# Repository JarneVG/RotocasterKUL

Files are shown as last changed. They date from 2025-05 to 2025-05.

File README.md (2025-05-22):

# RotocasterKUL
This is the accompanying report and documentation for the rotocasting machine, made in 2025 for the KU Leuven soft robotics research team.

## Software
Here, you can find the main code under RotocasterMainFirmware (arduino .ino files) as well as other people's libraries used for this project.

I changed some of these libraries to add or change functionalities, so be sure to add the ones you find here to your Arduino -> libraries directory

You should also have the Earle Philhowers Arduino Pico core installed.

Some useful tutorials for uploading:

https://learn.adafruit.com/rp2040-arduino-with-the-earlephilhower-core/installing-the-earlephilhower-core

https://randomnerdtutorials.com/programming-raspberry-pi-pico-w-arduino-ide/

## Electrical Hardware
The KiCAD design files can be found here. If there is something that needs to change, you can find the current version of the project here. The small problems with the current version are already implemented.

## Mechanical Hardware
A .step file is uploaded here to get a better grasp of what might be going on under the covers. This is not a build guide, rather part of the documentation.
Same thing for the bill of materials, where you can find all the parts used in this project

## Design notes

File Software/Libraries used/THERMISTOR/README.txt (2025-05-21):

## Original repository

https://github.com/panStamp/thermistor.git

Basic library that reads a NTC thermistor from an analog pin. Calculations relie on
Steinhart–Hart equation:

https://en.wikipedia.org/wiki/Thermistor#Steinhart.E2.80.93Hart_equation

See the example for more information.

Example of use with panStamp:
https://github.com/panStamp/panstamp/wiki/Temperature-measurement-with-cheap-NTC's

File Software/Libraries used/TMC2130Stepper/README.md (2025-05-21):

## Original repository

https://github.com/teemuatlut/TMC2130Stepper.git

# TMC2130Stepper
Arduino library for Trinamic TMC2130 Stepper driver

## TODO:
- [ ] Comments
- [x] Documentation
- [x] Examples
- [x] Easy setup for NEMA17 with default settings
- [x] Convert functions returning 0/1 to boolean
- [ ] Fritzing image of the wiring for an example setup

## Installation:

Use the Arduino IDE library manager (Sketch -> Include library -> Manage libraries...)

Search for TMC2130Stepper and then install.

Or download the zip file from Github and extract it to<br>
your-scetchbook-location/libraries<br>
and restart the IDE.

or goto to you arduino libraries folder and in command line
    git clone https://github.com/teemuatlut/TMC2130Stepper.git

## What works:
Nearly all the features in the registeries are configurable through get/set functions. See below for a list of functions. Datasheet ([link](https://www.trinamic.com/fileadmin/assets/Products/ICs_Documents/TMC2130_datasheet.pdf)) from Trinamic also provides further detail into the settings available.

## Simple example
```cpp
/*
Initializes the library and turns the motor in alternating directions.
*/
#define EN_PIN    38  // Nano v3:	16 Mega:	38	//enable (CFG6)
#define DIR_PIN   55  //			19			55	//direction
#define STEP_PIN  54  //			18			54	//step
#define CS_PIN    40  //			17			64	//chip select

bool dir = true;

#include <TMC2130Stepper.h>
TMC2130Stepper TMC2130 = TMC2130Stepper(EN_PIN, DIR_PIN, STEP_PIN, CS_PIN);

void setup() {
	Serial.begin(9600);
	TMC2130.begin(); // Initiate pins and registeries
	TMC2130.SilentStepStick2130(600); // Set stepper current to 600mA
	TMC2130.stealthChop(1); // Enable extremely quiet stepping
	
	digitalWrite(EN_PIN, LOW);
}

void loop() {
	digitalWrite(STEP_PIN, HIGH);
	delayMicroseconds(10);
	digitalWrite(STEP_PIN, LOW);
	delayMicroseconds(10);
	uint32_t ms = millis();
	static uint32_t last_time = 0;
	if ((ms - last_time) > 2000) {
		if (dir) {
			Serial.println("Dir -> 0");
			TMC2130.shaft_dir(0);
		} else {
			Serial.println("Dir -> 1");
			TMC2130.shaft_dir(1);
		}
		dir = !dir;
		Serial.println(TMC2130.GCONF(), BIN);
		last_time = ms;
	}
}
```

## Current calculations

A simple way to set the current is to use the setCurrent() method.

    I_rms = (CS+1)/32 * V_fs/(R_sense+0.02mOhm) * 1/sqrt(2)
    I_motor = I_sine/248 * (CS+1/32) * V_fs/(R_sense+0.02mOhm)

Where:<br>
I_rms is the rms current<br>
I_motor is the motor current<br>
CS is the Current Scale value<br>
V_fs is the voltage determined by v_sense<br>
R_sense is the chosen sense resistor<br>
I_sine is the current position in the sine table. I_motor reaches peak value at I_sine = 248<p>

If external_ref is enabled, V_fs is scaled by V_ain/2.5V

## Functions

Function 			| Argument range | Returns | Description
--------------------|-----|---|-----------------------------
begin 				|  -  | - | Initialized pins Enable, Direction, Step and Chip Select.<br>Initialized the SPI pins MOSI, MISO and SCK.<br>Calls spi.begin()<br>Sets off_time = 2 and blank_time = 24
setCurrent			|  0..2000<br>0.1 .. 1<br>0..1 | - | Helper function to set the motor RMS current.<br>Arguments:<br><b>uint16_t</b> Desired current in milliamps<br><b>float</b> Sense resistor value<br><b>float</b> Multiplier for holding current<br>Example for SilentStepStick2130: setCurrent(1200, 0.11, 0.5)<p>Makes use of the run_current() and hold_current() funtions.
SilentStepStick2130 |  0..2000  | - | Calls the begin() functions and according to the argument sets the current with sense resistor being 0.11 and multiplier being 0.5

## Register functions:

Note: You can read the saved value by calling a function without providing an argument.

### GCONF register
Function 			| Argument range | Returns | Description
--------------------|-----|---------|-----------------------------
GCONF 				|  -  | uint32_t| Read actual bits from the register
external_ref 		| 0/1 | bool | Use external voltage reference for coil currents
internal_sense_R 	| 0/1 | bool | Use internal sense resistors
stealthChop 		| 0/1 | bool | Enable stealthChop (dependant on velocity thresholds)
commutation 		| 0/1 | bool | Enable commutation by full step encoder
shaft_dir 			| 0/1 | bool | Inverse motor direction
diag0_errors 		| 0/1 | bool | Enable DIAG0 active on driver errors: Over temperature (ot), short to GND (s2g), undervoltage chargepump (uv_cp)
diag0_temp_prewarn 	| 0/1 | bool | Enable DIAG0 active on driver over temperature prewarning
diag0_stall 		| 0/1 | bool | Enable DIAG0 active on motor stall (set TCOOLTHRS before using this feature)
diag1_stall 		| 0/1 | bool | Enable DIAG1 active on motor stall (set TCOOLTHRS before using this feature) 
diag1_index 		| 0/1 | bool | Enable DIAG1 active on index position (microstep look up table position 0) 
diag1_chopper_on 	| 0/1 | bool | Enable DIAG1 active when chopper is on
diag1_steps_skipped | 0/1 | bool | Enable output toggle when steps are skipped in dcStep mode (increment of LOST_STEPS). Do not enable in conjunction with other DIAG1 options. 
diag0_active_high 	| 0/1 | bool | Set DIAG0 to active high
diag1_active_high 	| 0/1 | bool | Set DIAG1 to active high
small_hysteresis 	| 0/1 | bool | <b>0:</b> Hysteresis for step frequency comparison is 1/16 <br><b>1:</b> Hysteresis for step frequency comparison is 1/32
stop_enable 		| 0/1 | bool | Emergency stop: DCIN stops the sequencer when tied high (no steps become executed by the sequencer, motor goes to standstill state).
direct_mode 		| 0/1 | bool | Motor coil currents and polarity are directly controlled by the SPI interface.

### IHOLD_IRUN register
Function 		| Argument 	| Returns | Description
----------------|-----------|---------|-----------------------------
hold_current 	| 0..31 	| uint8_t | Standstill current (0=1/32…31=32/32)
run_current 	| 0..31 	| uint8_t | Motor run current (0=1/32…31=32/32)
hold_delay 		| 0..15 	| uint8_t | Controls the number of clock cycles for motor power down after a motion as soon as standstill is detected (stst=1) and TPOWERDOWN has expired. 

### REG_TPOWERDOWN register
Function 		 | Argument | Returns 	| Description
-----------------|----------|-----------|-----------------------------
power_down_delay | 0..255 	| uint8_t  	| power_down_delay sets the delay time after stand still (stst) of the motor to motor current power down. Time range is about 0 to 4 seconds. <br>0…((2^8)-1) * 2^18 tCLK 

### REG_TSTEP register
Function 		| Argument 	| Returns  | Description
----------------|-----------|----------|-----------------------------
microstep_time 	| - 		| uint32_t | Read the actual measured time between two 1/256 microsteps derived from the step input frequency in units of 1/fCLK. 

### REG_TPWMTHRS register
Function 			| Argument 		| Returns	| Description
--------------------|---------------|-----------|-----------------------------
stealth_max_speed 	| 0..1,048,575 	| uint32_t 	| This is the upper velocity for stealthChop voltage PWM mode. TSTEP ≥ TPWMTHRS - stealthChop PWM mode is enabled, if configured - dcStep is disabled 

### REG_TCOOLTHRS register
Function 			| Argument 		| Returns 	| Description
--------------------|---------------|-----------|-----------------------------
coolstep_min_speed 	| 0..1,048,575 	| uint32_t 	| This is the lower threshold velocity for switching on smart energy coolStep and stallGuard feature. 

### REG_THIGH register
Function 		| Argument 		| Returns 	| Description
----------------|---------------|-----------|-----------------------------
mode_sw_speed 	| 0..1,048,575 	| uint32_t  | This velocity setting allows velocity dependent switching into a different chopper mode and fullstepping to maximize torque. 

### REG_XDRIRECT register
Function 		| Argument 		| Returns 	| Description
----------------|---------------|-----------|-----------------------------
coil_A_current 	| -255..+255 	| int16_t  	| Specifies Motor coil currents and polarity directly programmed via the serial interface. In this mode, the current is scaled by IHOLD setting. 
coil_B_current 	| -255..+255 	| int16_t  	| As above.

### REG_VDCMIN register
Function 			| Argument 		| Returns 	| Description
--------------------|---------------|-----------|-----------------------------
DCstep_min_speed 	| 0..8,388,607 	| uint32_t  | The automatic commutation dcStep becomes enabled by the external signal DCEN. VDCMIN is used as the minimum step velocity when the motor is heavily loaded. <br>Hint: Also set DCCTRL parameters in order to operate dcStep.

### REG_CHOPCONF register
Function 				| Argument  | Returns 	| Description
------------------------|-----------|-----------|-----------------------------
CHOPCONF 				| - 		| uint32_t 	| Read actual bits from the register
off_time 				| 0..15 	| uint8_t 	| Off time setting controls duration of slow decay phase<br>NCLK= 12 + 32*TOFF<br>Initialized to value 2 (NCLK = 76) by begin()
hysteresis_start 		| 1..8 		| uint8_t 	| Add 1, 2, …, 8 to hysteresis low value HEND (1/512 of this setting adds to current setting) Attention: Effective HEND+HSTRT ≤ 16. Hint: Hysteresis decrement is done each 16 clocks
fast_decay_time 		| 0..15 	| uint8_t 	| Fast decay time setting TFD with  NCLK= 32*HSTRT
hysteresis_end 			| -3..12	| int8_t 	| This is the hysteresis value which becomes used for the hysteresis chopper. 
sine_offset 			| -3..12	| int8_t 	| This is the sine wave offset and 1/512 of the value becomes added to the absolute value of each sine wave entry.
disable_I_comparator 	| 0/1		| bool 	| <b>1:</b> Disables current comparator usage for termination of the fast decay cycle.<br>chopper_mode needs to be 1.
random_off_time 		| 0/1		| bool 	| <b>0:</b> Chopper off time is fixed as set by TOFF <br><b>1:</b> Random mode, TOFF is random modulated by dNCLK= -12 … +3 clocks. 
chopper_mode 			| 0/1		| uint8_t 	| <b>0:</b> Standard mode (spreadCycle) <br><b>1:</b> Constant off time with fast decay time.  <br>Fast decay time is also terminated when the negative nominal current is reached. Fast decay is after on time. 
blank_time 				| 16, 24,<br>36, 54| uint8_t | Set comparator blank time to 16, 24, 36 or 54 clocks. <br>Hint: 24 or 36 is recommended for most applications<br>Initialized to 36 (register value = 3) by begin()
high_sense_R 			| 0/1 		| bool 	| <b>0:</b> Low sensitivity, high sense resistor voltage <br><b>1:</b> High sensitivity, low sense resistor voltage 
fullstep_threshold 		| 0/1		| bool 	| This bit enables switching to fullstep, when VHIGH is exceeded. Switching takes place only at 45° position. The fullstep target current uses the current value from the microstep table at the 45° position. 
high_speed_mode 		| 0/1		| bool 	| This bit enables switching to chm=1 and fd=0, when VHIGH is exceeded. This way, a higher velocity can be achieved. Can be combined with vhighfs=1. If set, the TOFF setting automatically becomes doubled during high velocity operation in order to avoid doubling of the chopper frequency. 
sync_phases 			| 0..15		| bool 	| Synchronization of the chopper for both phases of a two phase motor in order to avoid the occurrence of a beat, especially at low motor velocities. It is automatically switched off above VHIGH.
microsteps 				| 255, 128, 64, 32, 16,<br>8, 4, 2, 0 (FULLSTEP) | uint8_t | Reduced microstep resolution for Step/Dir operation. The resolution gives the number of microstep entries per sine quarter wave.
interpolate 			| 0/1 		| bool 	| The actual microstep resolution becomes extrapolated to 256 microsteps for smoothest motor operation.
double_edge_step 		| 0/1 		| bool 	| Enable step impulse at each step edge to reduce step frequency requirement. 
disable_short_protection| 0/1 		| bool 	| <b>0:</b> Short to GND protection is on <br><b>1:</b> Short to GND protection is disabled 

### REG_COOLCONF register
Function 			| Argument 	 | Returns  | Description
--------------------|------------|----------|-----------------------------
COOLCONF 			| - 		 | uint32_t | Read actual bits from the register
sg_min 				| 0..15 	 | uint8_t 	| If the stallGuard2 result falls below sg_min*32, the motor current becomes increased to reduce motor load angle.
sg_max 				| 0..15 	 | uint8_t 	| If the stallGuard2 result is equal to or above (sg_min+sg_max+1)*32, the motor current becomes decreased to save energy. 
sg_step_width 		| 1, 2, 4, 8 | uint8_t 	| Current increment steps per measured stallGuard2 value
sg_current_decrease | 1, 2, 8, 32| uint8_t 	| For each (value) stallGuard2 values decrease by one 
smart_min_current 	| uint8_t 	 | uint8_t 	| <b>0:</b> 1/2 of current setting (IRUN)<br><b>1:</b> 1/4 of current setting (IRUN) 
sg_stall_value		| int8_t 	 | int8_t  	| This signed value controls stallGuard2 level for stall output and sets the optimum measurement range for readout. A lower value gives a higher sensitivity. Zero is the starting value working with most motors.  -64 to +63:  A higher value makes stallGuard2 less sensitive and requires more torque to indicate a stall. 
sg_filter 			| uint8_t 	 | uint8_t 	| <b>0:</b> Standard mode, high time resolution for stallGuard2<br><b>1:</b> Filtered mode, stallGuard2 signal updated for each four fullsteps (resp. six fullsteps for 3 phase motor) only to compensate for motor pole tolerances 

### REG_PWMCONF register
Function | Argument | Returns | Description
--------------------|-----------|----------|-----------------------------
PWMCONF 			| - 		| uint32_t | Read actual bits from the register
stealth_amplitude 	| 0..255 	| uint8_t  | pwm_ autoscale=0 <br>User defined  PWM amplitude offset (0-255) The resulting amplitude (limited to 0…255) is: PWM_AMPL + PWM_GRAD * 256 / TSTEP <p>pwm_ autoscale=1 <br>User defined maximum PWM amplitude when switching back from current chopper mode to voltage PWM mode (switch over velocity defined by TPWMTHRS). Do not set too low values, as the regulation cannot measure the current when the actual PWM value goes below a setting specific value. Settings above 0x40 recommended. 
stealth_gradient 	| 0..255 	| uint8_t  | pwm_ autoscale=0 <br>Velocity dependent gradient for PWM amplitude:  PWM_GRAD * 256 / TSTEP  is added to PWM_AMPL <p>pwm_ autoscale=1 <br>User defined  maximum PWM amplitude change per half wave (1 to 15) 
stealth_freq 		| 0..3 		| uint8_t  | <b>0:</b> fPWM=2/1024 fCLK<br><b>1:</b> fPWM=2/683 fCLK<br><b>2:</b> fPWM=2/512 fCLK<br><b>3:</b> fPWM=2/410 fCLK
stealth_autoscale 	| 0/1		| bool     | <b>0:</b> User defined PWM amplitude. The current settings have no influence.<br><b>1:</b> Enable automatic current control Attention: When using a user defined sine wave table, the amplitude of this sine wave table should not be less than 244. Best results are obtained with 247 to 252 as peak values.
stealth_symmetric 	| 0/1	 	| bool     | <b>0:</b> The PWM value may change within each PWM cycle (standard mode)<br><b>1:</b> A symmetric PWM cycle is enforced 
standstill_mode 	| 0..3		| uint8_t  | Stand still option when motor current setting is zero (I_HOLD=0).<br><b>0:</b>  Normal operation<br><b>1:</b>  Freewheeling<br><b>2:</b> Coil shorted using LS drivers<br><b>3:</b>  Coil shorted using HS drivers 

### REG_DRVSTATUS register
Function 	| Argument 	| Returns 	| Description
------------|-----------|-----------|-----------------------------
DRVSTATUS 	| - 		| uint32_t 	| Read actual bits from the register

### REG_PWM_SCALE register
Function 	| Argument 	| Returns 	| Description
------------|-----------|-----------|-----------------------------
PWM_SCALE 	| - 		| uint32_t 	| Read actual bits from the register

### REG_ENCM_CTRL register
Function 		| Argument 	| Returns 	| Description
----------------|-----------|-----------|-----------------------------
invert_encoder 	| 0/1 		| bool  	| Invert encoder inputs
maxspeed 		| 0/1	 	| bool  	| Ignore Step input. If set, the hold current IHOLD determines the motor current, unless a step source is activated

### REG_LOST_STEPS register
Function 	| Argument 	| Returns 	| Description
------------|-----------|-----------|-----------------------------
LOST_STEPS 	| - 		| uint32_t 	| Read actual bits from the register

### Read raw registry:

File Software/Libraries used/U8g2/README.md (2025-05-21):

# Original repository

https://github.com/ArduinoGetStarted/buzzer.git

# U8g2_Arduino: Arduino Monochrome Graphics Library

https://raw.githubusercontent.com/wiki/olikraus/u8g2/img/uc1701_dogs102_uno_board_320.jpg 

U8glib V2 library for Arduino

Description: https://github.com/olikraus/u8g2/wiki

Issue Tracker: https://github.com/olikraus/u8g2/issues

Download (2.35.30): https://github.com/olikraus/U8g2_Arduino/archive/master.zip

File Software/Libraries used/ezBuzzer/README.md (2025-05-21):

## Original repository

https://github.com/ArduinoGetStarted/buzzer.git

## Buzzer Library for Arduino - ezBuzzer
This library is designed for buzzer to beep or play memody without blocking other code.

**ezBuzzer** stands for **easy buzzer**, which mean that the library is easy to use.

Features
----------------------------
* Supports beep
* Supports melody
* All functions are non-blocking (no delay() function)

Available Examples
----------------------------
* [Beep](https://arduinogetstarted.com/library/arduino-beep-example)
* [Melody](https://arduinogetstarted.com/library/arduino-melody-example)
* [MelodyRepeat](https://arduinogetstarted.com/library/arduino-melody-repeat-example)

Available Functions
----------------------------
* ezBuzzer()
* stop()
* beep()
* playMelody()
* getState()
* loop()

How To Install the Library
----------------------------
* [ezBuzzer Library Installization Guide](https://arduinogetstarted.com/tutorials/arduino-buzzer-library)

References
----------------------------
* [ezBuzzer Library Reference](https://arduinogetstarted.com/tutorials/arduino-buzzer-library)

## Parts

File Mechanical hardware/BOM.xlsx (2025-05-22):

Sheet: BOM
item nr | Category | Part | Supplier Part # | Number | # needed | Cost/Article | Total cost | Supplier | Date of order | Date of arrival | Link | Idx
 | Electrical |  |  |  |  |  |  |  |  |  |  | 1
 | Interface |  |  | €30.91 |  |  |  |  |  |  |  | 2
1 |  | Rotary push button |  | 1 | 1 | €2.63 | €2.63 | Farnell | 2025-02-28 | 2025-03-06 | https://be.farnell.com/bourns/pec11l-4120f-s0020/encoder-quadrature-20ppr-60rpm/dp/4014825 | 3
2 |  | Oled screen .95" |  | 1 | 1 | €17.29 | €17.29 | Farnell | 2025-02-28 |  |  | 4
3 |  | LCD screen | 2436023 - 62 | 1 | 1 | €10.99 | €10.99 | Conrad | 2025-03-26 | 2025-04-03 | https://www.conrad.be/nl/p/joy-it-lc-display-wit-blauw-128-x-64-pixel-b-x-h-x-d-93-x-70-x-12-mm-2436023.html | 5
 |  |  |  |  |  |  |  |  |  |  |  | 6
 | Safety |  |  | €49.43 |  |  |  |  |  |  |  | 7
4 |  | Door limit switch | DEL00005 | 1 | 1 | €3.85 | €3.85 | 123-3D | 2025-03-26 | 2024-04-10 | https://www.123-3d.nl/123-3D-Microswitch-eindstop-met-1-meter-kabel-i1725-t324.html | 8 | https://www.123-3d.nl/123-3D-Microswitch-eindstop-i974-t324.html
5 |  | E-stop | 2748226 | 1 | 1 | €12.98 | €12.98 | Farnell | 2025-03-26 | 2025-04-03 | https://be.farnell.com/multicomp-pro/mca20l-v4e10q7r/emergency-stop-sw-spst-no-120v/dp/2748226 | 9 | https://benl.rs-online.com/web/p/emergency-stop-push-buttons/0102713
6 |  | Actual E-stop | 704622 - 62 | 1 | 1 | €9.49 | €9.49 | Conrad |  | 2025-04-22 | https://www.conrad.be/nl/p/tru-components-las0-a3y-11ts-noodstopschakelaar-250-v-ac-5-a-1x-nc-1x-no-ip40-1-stuk-s-704622.html | 10
7 |  | Resettable fuse for heater | 2786604 | 1 | 1 | €1.28 | €1.28 | farnell | 2025-03-26 | 2025-04-03 | https://nl.farnell.com/littelfuse/ahef750/fuse-resettable-ptc-32vdc-7-5a/dp/2786604 | 11
8 |  | Fuse holder 20A |  | 1 | 1 | €1.08 | €1.08 | RS Components |  | 2025-04-22 | https://benl.rs-online.com/web/p/fuse-blocks/1884617?gb=s | 12
9 |  | Car fuse for heater 20A | 787-4151P | 10 | 1 | €0.28 | €2.81 | RS Components |  | 2025-04-22 | https://benl.rs-online.com/web/p/car-fuses/7874151P?gb=s | 13
 |  |  |  |  |  |  |  |  |  |  |  | 14
 | Heating |  |  | €28.94 |  |  |  |  |  |  |  | 15
10 |  | Heater + fan | B07Y24KVPQ | 1 | 1 | €13.09 | €13.09 | Amazon NL | 2025-03-26 | 2025-04-03 | https://www.amazon.nl/Constante-Temperatuur-PTC-ventilator-Autoverwarmer-Ruimteverwarmingsincubator/dp/B07YTL7DFK?__mk_nl_NL=%C3%85M%C3%85%C5%BD%C3%95%C3%91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 (https://www.amazon.nl/-/en/Nikou-Air-Heater-Constant-Temperature/dp/B07Y24KVPQ) | 16
11 |  | Thermo sensor (thermistor) | 4128286 | 1 | 1 | €4.85 | €4.85 | Farnell | 2025-03-26 | 2025-04-03 | https://be.farnell.com/molex/218534-3617/thermistor-ntc-3600k-10-kohm/dp/4128286 | 17
12 |  | Heat sink TO-220 | 189-9132 | 1 | 1 | €1.52 | €1.52 | RS Components | 2025-03-26 | 2025-04-04 | https://benl.rs-online.com/web/p/heatsinks/1899132?matchtype=&gad_source=1&gclsrc=aw.ds | 18
13 |  | Heat sink Pico | 3133389 - 62 | 1 | 1 | €1.49 | €1.49 | Conrad | 2025-03-26 | 2025-04-03 | https://www.conrad.be/nl/p/joy-it-rb-heatsink-b-koellichaamset-geschikt-voor-serie-raspberry-pi-banana-pi-asus-tinker-board-radxa-zwart-3133389.html | 19
14 |  | Pico cooling fan | 1720600 - 62 | 1 | 1 | €3.29 | €3.29 | Conrad | 2025-03-26 | 2025-04-03 | https://www.conrad.be/nl/p/joy-it-sbc-fan-303010-actieve-ventilator-geschikt-voor-serie-raspberry-pi-rock-pi-banana-pi-zwart-1720600.html | 20
15 |  | Electronics cooling fan | DMO00037 | 1 | 1 | €4.70 | €4.70 | 123-3D |  | 2025-04-22 | https://www.123-3d.nl/123-3D-Ventilator-24V-50x50x12-mm-axiaal-i2705-t15055.html | 21
 |  |  |  |  |  |  |  |  |  |  |  | 22 | https://www.tinytronics.nl/nl/mechanica-en-actuatoren/motoraansturingen-en-drivers/stappen-motoraansturingen-en-drivers/bigtreetech-tmc2130-v3.0-stappenmotord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
 | Compute |  |  | €39.64 |  |  |  |  |  |  |  | 23
16 |  | Stepper driver |  | 2 | 2 | €17.50 | €35.00 | 123-3D | 2025-03-26 | 2024-04-10 | https://www.123-3d.nl/BigTreeTech-TMC2130-Stappendriver-1-256-stap-interpolatie-v3-0-SPI-1020000132-ZZB000296-i8343-t332.html | 24
17 |  | Raspberry Pi Pico | 3643332 | 1 | 1 | €4.64 | €4.64 | Farnell | 2025-03-26 | 2025-04-03 | https://be.farnell.com/raspberry-pi/raspberry-pi-pico/raspberry-pi-32bit-arm-cortex/dp/3643332 | 25
 |  |  |  |  |  |  |  |  |  |  |  | 26
 | Power |  |  | €52.33 |  |  |  |  |  |  |  | 27
18 |  | Main power supply (220AC -> 24DC) | B077CK3NXY | 1 | 1 | €36.99 | €36.99 | Amazon BE | 2025-03-26 | 2025-04-03 | https://www.amazon.com.be/-/nl/industri%C3%ABle-omvormer-elektrische-printer-verwarming/dp/B077CK3NXY | 28
19 |  | Arduino power supply (24DC -> 5 DC) | DAR00071 | 1 | 1 | €6.05 | €6.05 | 123-3D | 2025-03-26 | 2024-04-10 | https://www.123-3d.nl/123-3D-Step-down-DC-DC-converter-3-2-40-V-DC-naar-1-25-35-V-DC-2-A-i3869-t13129.html | 29
20 |  | IEC C14 power socket with fuse & switch | 501638 - 62 | 1 | 1 | €5.00 | €5.00 | Conrad | 2025-03-26 | 2025-04-03 | https://www.conrad.be/nl/p/501638-apparaatstekker-koud-stekker-inbouw-verticaal-totaal-aantal-polen-2-pe-10-a-zwart-1-stuk-s-501638.html | 30
21 |  | Power cable 2m EU socket to IEC C13 | 2521346 - 62 | 1 | 1 | €4.29 | €4.29 | Conrad | 2025-03-26 | 2025-04-03 | https://www.conrad.be/nl/p/sygonix-sy-5042692-apparaat-koud-aansluitkabel-zwart-2-00-m-2521346.html | 31
 |  |  |  |  |  |  |  |  |  |  |  | 32
 | PCB |  |  | €15.02 |  |  |  |  |  | 2025-04-22 |  | 33
22 |  | n mosfet IRLZ44N | 162877 - 62 | 3 | 3 | €0.93 | €2.79 | Conrad | 2025-03-26 | 2025-04-03 | https://www.conrad.be/nl/p/infineon-technologies-irlz44npbf-mosfet-1-hexfet-110-w-to-220-162877.html | 34
23 |  | n mosfet IRL3705NPBF | 162784 - 62 | 1 | 1 | €2.29 | €2.29 | Conrad | 2025-03-26 | 2025-04-03 | https://www.conrad.nl/nl/p/infineon-technologies-irl3705npbf-mosfet-1-n-kanaal-170-w-to-220-162784.html | 35
24 |  | n mosfet IRLB3034PBF Low RdsOn | 161162 - 62 | 1 | 1 | €3.99 | €3.99 | Conrad |  | 2025-04-22 | https://www.conrad.be/nl/p/infineon-technologies-irlb3034pbf-mosfet-1-n-kanaal-375-w-to-220ab-161162.html?gad_source=1 | 36
25 |  | 100nF 0603 capacitors | 257-1091 | 50 | 8 | €0.03 | €1.40 | RS Components | 2025-03-26 | 2025-04-04 | https://benl.rs-online.com/web/p/mlccs-multilayer-ceramic-capacitors/2571091?gb=s | 37
26 |  | 10k 0603 resistors | 199-1659 | 20 | 12 | €0.03 | €0.64 | RS Components | 2025-03-26 | 2025-04-04 | https://benl.rs-online.com/web/p/surface-mount-resistors/1991659?gb=s | 38
27 |  | LED Strip 1m, 24VDC, Natural White |  | 1 | 1 | €3.91 | €3.91 | AliExpress | 2025-03-26 | 2025-04-03 | https://www.aliexpress.com/item/1005005576519990.html?mp=1 | 39
 |  |  |  |  |  |  |  |  |  |  |  | 40
 | Connectors |  |  | €20.56 |  |  |  |  |  |  |  | 41
28 |  | Female header (40 pins) | 1303521 - 62 | 5 | 3 | €0.75 | €3.75 | Conrad | 2025-03-26 | 2025-04-03 | https://www.conrad.be/nl/p/econ-connect-female-header-standaard-aantal-rijen-1-aantal-polen-per-rij-40-bl40-1g8-1-stuk-s-1303521.html | 42
29 |  | Male header (30 pins) | 1390106 - 62 | 7 | 2 | €0.44 | €3.08 | Conrad | 2025-03-26 | 2025-04-03 | https://www.conrad.be/nl/p/connfly-male-header-standaard-aantal-rijen-1-aantal-polen-per-rij-30-ds1021-1-30sf11-1-stuk-s-1390106.html | 43
30 |  | JST XH 4p Male 2.5mm | 820-1551 | 5 | 4 | €0.25 | €1.25 | RS Components | 2025-03-26 | 2025-04-04 | https://benl.rs-online.com/web/p/pcb-headers/8201551?gb=s | 44
31 |  | JST XH 4p Female 2.5mm | 820-1618 | 5 | 4 | €0.13 | €0.63 | RS Components | 2025-03-26 | 2025-04-04 | https://benl.rs-online.com/web/p/wire-housings-plugs/8201618?gb=s | 45
32 |  | JST XH 5p Male 2.5mm | 820-1560 | 5 | 1 | €0.32 | €1.61 | RS Components | 2025-03-26 |  | https://benl.rs-online.com/web/p/pcb-headers/8201560?gb=s | 46
33 |  | JST XH 5p Female 2.5mm | 820-1627 | 5 | 1 | €0.15 | €0.76 | RS Components | 2025-03-26 | 2025-04-04 | https://benl.rs-online.com/web/p/wire-housings-plugs/8201627?gb=s | 47
34 |  | JST XH 2p Male 2.5mm | 820-1554 | 5 | 2 | €0.18 | €0.92 | RS Components | 2025-03-26 | 2025-04-04 | https://benl.rs-online.com/web/p/pcb-headers/8201554?gb=s | 48
35 |  | JST XH 2p Female 2.5mm | 820-1611 | 5 | 2 | €0.11 | €0.55 | RS Components | 2025-03-26 | 2025-04-04 | https://benl.rs-online.com/web/p/wire-housings-plugs/8201611?gb=s | 49
36 |  | High Current Terminal Block | 790-1064 | 10 | 6 | €0.61 | €6.12 | RS Components | 2025-03-26 | 2025-04-04 | https://benl.rs-online.com/web/p/pcb-terminal-blocks/7901064?gb=s | 50
 |  |  |  |  |  |  |  |  |  |  |  | 51
37 |  | JST XH Female Crimp | 373-4188 | 100 | 25 | €0.02 | €1.90 | RS Components | 2025-03-26 | 2025-04-04 | https://benl.rs-online.com/web/p/crimp-contacts/3734188?gb=s | 52
38 |  | Thick current wires |  |  |  |  |  |  |  |  |  | 53
39 |  | 18 AWG Ferrules (to crimp wire ends) | 2758836 | 20 | 12 | €0.08 | €1.65 | Farnell | 2025-03-26 | 2025-04-03 | https://be.farnell.com/en-BE/wago/216-203/terminal-wire-ferrule-18awg-red/dp/2758836 | 54
 |  |  |  |  |  |  |  |  |  |  |  | 55
 | subtotal (incl btw) |  |  |  |  |  | €218.90 | €172.93 |  |  |  | 56
 |  |  |  |  |  |  |  |  |  |  |  | 57
 | Mechanical |  |  |  |  |  |  |  |  |  |  | 58
 | Frame |  |  | €129.54 |  |  |  |  |  |  |  | 59
40 |  | 20x20 Aluminium extrusion 575 mm |  | 4 |  | €3.89 | €15.55 | Aluxprofile | 2025-03-26 | 2025-04-03 | https://www.aluxprofile.com/aluminium-slot-profile-2020-v-slot/a3663?filter=38 | 60
41 |  | 20x20 Aluminium extrusion 630 mm |  | 4 |  | €4.25 | €17.02 | Aluxprofile | 2025-03-26 | 2025-04-03 | https://www.aluxprofile.com/aluminium-slot-profile-2020-v-slot/a3663?filter=39 | 61
42 |  | 20x20 Aluminium extrusion 510 mm |  | 4 |  | €3.44 | €13.78 | Aluxprofile | 2025-03-26 | 2025-04-03 | https://www.aluxprofile.com/aluminium-slot-profile-2020-v-slot/a3663?filter=40 | 62
43 |  | 20x20 Aluminium extrusion 530 mm |  | 2 |  | €3.58 | €7.16 | Aluxprofile | 2025-03-26 | 2025-04-03 | https://www.aluxprofile.com/aluminium-slot-profile-2020-v-slot/a3663?filter=41 | 63
44 |  | 20x20 Aluminium extrusion 313 mm |  | 2 |  | €2.12 | €4.23 | Aluxprofile | 2025-03-26 | 2025-04-03 | https://www.aluxprofile.com/aluminium-slot-profile-2020-v-slot/a3663?filter=42 | 64
45 |  | 20x20 Aluminium extrusion 365 mm |  | 2 |  | €2.46 | €4.92 | Aluxprofile | 2025-03-26 | 2025-04-03 | https://www.aluxprofile.com/aluminium-slot-profile-2020-v-slot/a3663?filter=43 | 65
46 |  | 20x20 Aluminium extrusion 501 mm |  | 2 |  | €3.38 | €6.77 | Aluxprofile | 2025-03-26 | 2025-04-03 | https://www.aluxprofile.com/aluminium-slot-profile-2020-v-slot/a3663?filter=44 | 66
47 |  | 20x20 Aluminium extrusion 383 mm |  | 2 |  | €2.58 | €5.17 | Aluxprofile | 2025-03-26 | 2025-04-03 | https://www.aluxprofile.com/aluminium-slot-profile-2020-v-slot/a3663?filter=45 | 67
48 |  | Loctite blue 5ml | 442-3413 | 1 |  | €10.54 | €10.54 | RS Components | 2025-03-26 | 2025-04-04 | https://benl.rs-online.com/web/p/thread-lock/4423413?gb=s | 68
49 |  | Adjustable feet | 531001 | 4 |  | €0.80 | €3.20 | Misumi | 2025-03-26 | 2025-04-22 | https://uk.misumi-ec.com/vona2/detail/221006483028/?list=PageCategory | 69
50 |  | Slot covers 5m | DFC00177 | 5 | est ~23m | €7.34 | €36.70 | 123-3D | 2025-03-26 | 2024-04-10 | https://www.123-3d.nl/123-3D-Slot-cover-6-mm-voor-2020-profiel-Grijs-1-meter-i7488-t14575.html | 70
51 |  | End caps 10pc | DFC00108 | 1 |  | €4.50 | €4.50 | 123-3D | 2025-03-26 | 2024-04-10 | https://www.123-3d.nl/123-3D-Afdekkap-t-b-v-aluminium-profiel-20x20-10-stuks-123-3D-huismerk-091042S05-091332-i5256-t14575.html | 71
 |  |  |  |  |  |  |  |  |  |  |  | 72
 | Axles & bearings |  |  | €38.93 |  |  |  |  |  |  |  | 73
52 |  | 8mm precision rod 110 mm | PSFG8-110 | 1 |  | €4.94 | €4.94 | Misumi | 2025-03-26 | 2025-04-22 | https://uk.misumi-ec.com/vona2/detail/110302634310/ | 74
53 |  | 8mm precision rod 86 mm | PSFG8-86 | 1 |  | €3.08 | €3.08 | Misumi | 2025-03-26 | 2025-04-22 | https://uk.misumi-ec.com/vona2/detail/110302634310/ | 75
54 |  | 8mm precision rod 66 mm | PSFG8-66 | 1 |  | €3.08 | €3.08 | Misumi | 2025-03-26 | 2025-04-22 | https://uk.misumi-ec.com/vona2/detail/110302634310/ | 76
55 |  | 8mm precision rod 87 mm | PSFG8-87 | 1 |  | €3.08 | €3.08 | Misumi | 2025-03-26 | 2025-04-22 | https://uk.misumi-ec.com/vona2/detail/110302634310/ | 77
56 |  | KFL8 bearing flange block x2 | DFC00077 | 3 |  | €8.25 | €24.75 | 123-3D | 2025-03-26 | 2024-04-10 | https://www.123-3d.nl/123-3D-KFL8-lager-as-bevestiging-2-stuks-i3512-t13814.html | 78
 |  |  |  |  |  |  |  |  |  |  |  | 79
 | Belts & pulleys |  |  | €82.75 |  |  |  |  |  |  |  | 80
57 |  | GT2 pulley 60t 8mm bore 9mm belt | DME00112 | 2 |  | €10.00 | €20.00 | 123-3D | 2025-03-26 | 2024-04-10 | https://www.123-3d.nl/123-3D-GT2-Pulley-hoge-resolutie-9-mm-riem-60-tanden-8-mm-as-i2573-t14819.html | 81
58 |  | GT2 pulley 20t 8mm bore 9mm belt | DME00069 | 2 |  | €6.00 | €12.00 | 123-3D | 2025-03-26 | 2024-04-10 | https://www.123-3d.nl/123-3D-GT2-Pulley-hoge-resolutie-9-mm-riem-20-tanden-8-mm-as-i2306-t14819.html | 82
59 |  | GT2 pulley 20t 5mm bore 9mm belt | DME00068 | 2 |  | €6.00 | €12.00 | 123-3D | 2025-03-26 | 2024-04-10 | https://www.123-3d.nl/123-3D-GT2-Pulley-hoge-resolutie-9-mm-riem-20-tanden-5-mm-as-i2305-t14815.html | 83
60 |  | GT2 belt 9mm 726mm | GBN7262GT-90 | 2 |  | €11.45 | €22.90 | Misumi | 2025-03-26 | 2025-04-22 | https://uk.misumi-ec.com/vona2/detail/110302190510/ | 84
61 |  | GT2 belt 9mm 1078mm | 1078-2GT-9 | 0 |  | €20.11 | €0.00 | Misumi | 2025-03-26 |  | https://uk.misumi-ec.com/vona2/detail/221004924958/?list=PageCategory | 85
62 |  | GT2 belt 10mm 1040mm | 9mm/1040-2GT/1st | 1 |  | €3.53 | €3.53 | AliExpress | 2025-03-26 | 2025-04-03 | https://nl.aliexpress.com/item/32299384151.html?curPageLogUid=R1AIa9U5Uo5a&utparam-url=scene%3Asearch%7Cquery_from%3A | 86
63 |  | Flanged bearing 606HZZ1 | F606-H-ZZ1 | 4 |  | €1.20 | €4.80 | Misumi | 2025-03-26 | 2025-04-22 | https://uk.misumi-ec.com/vona2/detail/221000531116/?list=PageCategory | 87
64 |  | Eye bolt M6x50 | K1418.0650 | 2 |  | €3.76 | €7.52 | Misumi | 2025-03-26 | 2025-04-22 | https://uk.misumi-ec.com/vona2/detail/221303930205/?KWSearch=eye+bolt&searchFlow=results2products | 88
 |  |  |  |  |  |  |  |  |  |  |  | 89
 | Plate system |  |  | €66.31 |  |  |  |  |  |  |  | 90
65 |  | U-channel 15x15x2 | HFHC1515-2-270 | 2 |  | €3.75 | €7.50 | Misumi | 2025-03-26 | 2025-04-22 | https://uk.misumi-ec.com/vona2/detail/110300467020/?KWSearch=u+channel&searchFlow=results2products | 91
66 |  | Tight-Hold Draw Latch | 1794A51 | 2 |  | €7.29 | €14.58 | Mc Master | 2025-03-26 | 2025-04-03 | https://www.mcmaster.com/1794A51/ | 92
67 |  | PC plate 350x300x6 mm |  | 1 |  | €26.49 | €26.49 | Kunststofplaten.be | 2025-03-26 | 2025-04-22 | https://kunststofplaten.be/product/helder-polycarbonaat-6-mm/ | 93
68 |  | Nylon Plastic Adjustable Handle | 6324K11 | 2 |  | €6.29 | €12.58 | Mc Master | 2025-03-26 | 2025-04-03 | https://www.mcmaster.com/6324K11-6324K111/ | 94
69 |  | Knurled bolt plastic M4 | 24830.0036 | 4 |  | €1.29 | €5.16 | Misumi | 2025-03-26 | 2025-04-22 | https://uk.misumi-ec.com/vona2/detail/221005517968/?list=PageCategory | 95
 |  |  |  |  |  |  |  |  |  |  |  | 96
 |  |  |  |  |  |  |  |  |  |  |  | 97
 | Enclosure |  |  | €108.45 |  |  |  |  |  |  |  | 98
70 |  | PE-HD plate 3mm 630x615 |  | 1 |  | €13.64 | €13.64 | Kunststofplaten.be | 2025-03-26 | 2025-04-22 | https://kunststofplaten.be/product/hdpe-zwart-3-mm/ | 99
71 |  | PE-HD plate 3mm 630x550 |  | 2 |  | €12.18 | €24.35 | Kunststofplaten.be | 2025-03-26 | 2025-04-22 | https://kunststofplaten.be/product/hdpe-zwart-3-mm/ | 100
72 |  | PE-HD plate 3mm 615x550 |  | 1 |  | €12.17 | €12.17 | Kunststofplaten.be | 2025-03-26 | 2025-04-22 | https://kunststofplaten.be/product/hdpe-zwart-3-mm/ | 101
73 |  | PE-HD plate 3mm 613x548 |  | 1 |  | €11.80 | €11.80 | Kunststofplaten.be | 2025-03-26 | 2025-04-22 | https://kunststofplaten.be/product/hdpe-zwart-3-mm/ | 102
74 |  | PE-HD plate 3mm 615x100 |  | 1 |  | €3.63 | €3.63 | Kunststofplaten.be | 2025-03-26 | 2025-04-22 | https://kunststofplaten.be/product/hdpe-zwart-3-mm/ | 103
75 |  | PE-HD plate 3mm 548x215 |  | 1 |  | €4.14 | €4.14 | Kunststofplaten.be | 2025-03-26 | 2025-04-22 | https://kunststofplaten.be/product/hdpe-zwart-3-mm/ | 104
 |  |  |  |  |  |  |  |  |  |  |  | 105
76 |  | PC plate 4mm 615x550 |  | 1 |  | €23.91 | €23.91 | Kunststofplaten.be | 2025-03-26 | 2025-04-22 | https://kunststofplaten.be/product/helder-polycarbonaat-4-mm/ | 106
77 |  | Magnetic door catch | C-92-1 | 2 |  | €1.52 | €3.04 | Misumi | 2025-03-26 | 2025-04-22 | https://uk.misumi-ec.com/vona2/detail/221004904866/?list=PageCategory (https://kunststofplaten.be/product/hdpe-zwart-3-mm/) | 107
78 |  | Door handle | HHDS122 | 1 |  | €5.20 | €5.20 | Misumi | 2025-03-26 | 2025-04-22 | https://uk.misumi-ec.com/vona2/detail/110302595630/?list=PageCategory | 108
79 |  | Foam tape | 207-744 | 1 |  | €6.57 | €6.57 | RS Components | 2025-03-26 | 2025-04-04 | https://benl.rs-online.com/web/p/foam-tapes/0207744 | 109
 |  |  |  |  |  |  |  |  |  |  |  | 110
 | Motors |  |  | €17.94 |  |  |  |  |  |  |  | 111
80 |  | Nema 17 High torque | 17HE24-2104S | 2 |  | €8.97 | €17.94 | StepperOnline | 2025-03-26 | 2025-04-03 | https://www.omc-stepperonline.com/nl/e-serie-nema-17-stappenmotor-1-8deg-60ncm-84-97oz-in-2-1a-42x42x60mm-4-draden-17he24-2104s | 112
 |  |  |  |  |  |  |  |  |  |  |  | 113
 | 3D printing |  |  | €67.45 |  |  |  |  |  |  |  | 114
81 |  | PC 275 Traffic Black 1kg | SPC-80946 | 1 |  | €40.49 | €40.49 | 123-3D | 2025-03-26 | 2025-04-10 | https://www.3djake.be/nl-BE/spectrum/pc-275-traffic-black?sai=28335 | 115
82 |  | eASA Black 1kg | ESUNCN-ASA175B1Y1 | 1 |  | €24.74 | €24.74 | 123-3D | 2025-03-26 | 2025-04-10 | https://www.3djake.be/nl-BE/esun/easa-black?sai=11871 | 116
83 |  | Heat set insert M4x4 | BRM4-4.1 | 6 |  | €0.37 | €2.22 | Misumi | 2025-03-26 | 2025-04-22 | https://uk.misumi-ec.com/vona2/detail/221005351346/?list=PageCategory | 117
 |  |  |  |  |  |  |  |  |  |  |  | 118
 | Fasteners |  |  | €73.44 |  |  |  |  |  |  |  | 119
84 |  | Socket button head screw M6x16 | ISO 7380-M6x16 BLACK | 35 | 32 | €0.12 | €4.20 | Aluxprofile | 2025-03-26 | 2025-04-03 | https://www.aluxprofile.com/hexagon-socket-button-head-screw-iso-7380-m6x16-black/a3863?filter=58%2C24 | 120
85 |  | Socket button head screw M6x10 | CSHBTAN-ST-M6-16 | 10 | 2 | €0.30 | €3.00 | Misumi | 2025-03-26 | 2025-04-22 | https://uk.misumi-ec.com/vona2/detail/221005020282/?list=PageCategory | 121
86 |  | Socket button head screw M5x8 | CSHBTAN-ST-M5-8 | 85 | 81 | €0.07 | €5.95 | Misumi | 2025-03-26 | 2025-04-22 | https://uk.misumi-ec.com/vona2/detail/221005020282/?list=PageCategory | 122
87 |  | Socket button head screw M5x16 | CSHBTHT-ST-M5-16 | 10 | 4 | €0.24 | €2.40 | Misumi | 2025-03-26 | 2025-04-22 | https://uk.misumi-ec.com/vona2/detail/221005020293/?list=PageCategory | 123
88 |  | Socket button head screw M5x14 | CSHBTHT-ST-M5-14 | 10 | 6 | €0.24 | €2.40 | Misumi | 2025-03-26 | 2025-04-22 | https://uk.misumi-ec.com/vona2/detail/221005020293/?list=PageCategory | 124
89 |  | Socket button head screw M4x40 | CSHBTHT-ST-M4-40 | 10 | 6 | €0.37 | €3.70 | Misumi | 2025-03-26 | 2025-04-22 | Button Bolt with Hex Socket Head SSS Standard from TOKOSHA K | MISUMI (https://uk.misumi-ec.com/vona2/detail/221005020293/?list=PageCategory) | 125
90 |  | Socket button head screw M4x14 | CSHBTAN-ST-M4-14 | 4 | 4 | €0.04 | €0.16 | Misumi | 2025-03-26 | 2025-04-22 | Button Bolt with Hex Head Socket JIS-B1174 from NISSAN SCREW | MISUMI (https://uk.misumi-ec.com/vona2/detail/221005020282/?list=PageCategory) | 126
91 |  | Socket button head screw M4x6 | CSHBTAN-ST-M4-6 | 13 | 13 | €0.18 | €2.34 | Misumi | 2025-03-26 | 2025-04-22 | Button Bolt with Hex Head Socket JIS-B1174 from NISSAN SCREW | MISUMI (https://uk.misumi-ec.com/vona2/detail/221005020282/?list=PageCategory) | 127
92 |  | Socket button head screw M3x8 | CSHBTAN-ST-M3-8 | 4 | 4 | €0.36 | €1.44 | Misumi | 2025-03-26 | 2025-04-22 | Button Bolt with Hex Head Socket JIS-B1174 from NISSAN SCREW | MISUMI (https://uk.misumi-ec.com/vona2/detail/221005020282/?list=PageCategory) | 128
93 |  | Socket button head screw M3x10 | CSHBTAN-ST-M3-10 | 25 | 12 | €0.20 | €5.00 | Misumi | 2025-03-26 | 2025-04-22 | Button Bolt with Hex Head Socket JIS-B1174 from NISSAN SCREW | MISUMI (https://uk.misumi-ec.com/vona2/detail/221005020282/?list=PageCategory) | 129
94 |  | Socket button head screw M3x16 | CSHBT-SUS-M3-16 | 12 | 10 | €0.10 | €1.20 | Misumi | 2025-03-26 | 2025-04-22 | https://uk.misumi-ec.com/vona2/detail/221000551174/?list=PageCategory | 130
95 |  | Socket button head screw M3x40 | CSHBTHT-ST-M3-40 | 10 | 4 | €0.32 | €3.20 | Misumi | 2025-03-26 | 2025-04-22 | Button Bolt with Hex Socket Head SSS Standard from TOKOSHA K | MISUMI (https://uk.misumi-ec.com/vona2/detail/221005020293/?list=PageCategory) | 131
 |  |  |  |  |  |  |  |  |  |  |  | 132
96 |  | Socket head cap screw M6x50 | CSH-ST-M6-50 | 1 | 1 | €0.70 | €0.70 | Misumi | 2025-03-26 | 2025-04-22 | Hexagonal Socket Head Bolt (All Screws / Partial Thread Screw) [7 Types of Materials, 21 Types of Surface Treatment] from SUNCO | MISUMI (https://uk.misumi-ec.com/vona2/detail/221000551286/) | 133
97 |  | Socket head cap screw M4x25 | 91210.9425 | 3 | 3 | €0.05 | €0.15 | Misumi | 2025-03-26 | 2025-04-22 | Cheese head screw according to DIN 912 from BOELLHOFF | MISUMI (https://uk.misumi-ec.com/vona2/detail/221006347487/) | 134
98 |  | Socket head cap screw M2x10 | CSH-ST-M2-10 | 2 | 2 | €0.39 | €0.78 | Misumi | 2025-03-26 | 2025-04-22 | Hexagonal Socket Head Bolt (All Screws / Partial Thread Screw) [7 Types of Materials, 21 Types of Surface Treatment] from SUNCO | MISUMI (https://uk.misumi-ec.com/vona2/detail/221000551286/) | 135
99 |  | Socket head cap screw M2x5 | CSHH-ST-M2-5 | 4 | 4 | €0.30 | €1.20 | Misumi | 2025-03-26 | 2025-04-22 | Hex Socket Head Bolt CSHH / CSHHL from TOKOSHA K | MISUMI (https://uk.misumi-ec.com/vona2/detail/221005020259/?list=PageCategory) | 136
 |  |  |  |  |  |  |  |  |  |  |  | 137
100 |  | Socket countersunk head screw M5x16 | CSHCSHT-ST-M5-16 | 4 | 4 | €0.39 | €1.56 | Misumi | 2025-03-26 | 2025-04-22 | Flat Head Bolt with Hex Socket SSS Standard from TOKOSHA K | MISUMI (https://uk.misumi-ec.com/vona2/detail/221005020327/?list=PageCategory) | 138
101 |  | Socket countersunk head screw M3x5 | CSHCSHT-ST-M3-5 | 4 | 4 | €0.25 | €1.00 | Misumi | 2025-03-26 | 2025-04-22 | Flat Head Bolt with Hex Socket SSS Standard from TOKOSHA K | MISUMI (https://uk.misumi-ec.com/vona2/detail/221005020327/?list=PageCategory) | 139
102 |  | Socket countersunk head screw M3x12 | CSHCSHT-ST-M3-12 | 4 | 4 | €0.29 | €1.16 | Misumi | 2025-03-26 | 2025-04-22 | Flat Head Bolt with Hex Socket SSS Standard from TOKOSHA K | MISUMI (https://uk.misumi-ec.com/vona2/detail/221005020327/?list=PageCategory) | 140
 |  |  |  |  |  |  |  |  |  |  |  | 141
103 |  | Prevailing torque nut M6 | FNTLN-STU-M6 | 3 | 3 | €0.39 | €1.17 | Misumi | 2025-03-26 | 2025-04-22 | Flange Nylon Nut from SUNCO | MISUMI (https://uk.misumi-ec.com/vona2/detail/221000544941/?CategorySpec=00000232412%3A%3Ad&list=PageCategory) | 142
104 |  | Hex thin nut M3 | 004394129030000 | 100 | 8 | €0.03 | €3.00 | Misumi | 2025-03-26 | 2025-04-22 | DIN 439 Hexagon nuts from REYHER | MISUMI (https://uk.misumi-ec.com/vona2/detail/221006357466/?CategorySpec=00000230742%3A%3Amig00000002021409&list=PageCategory) | 143
105 |  | Square thin nut M5 | TBN-STC-M5 | 4 | 4 | €0.01 | €0.04 | Misumi | 2025-03-26 | 2025-04-22 | Bar Nuts from OKAMURA WORKS | MISUMI (https://uk.misumi-ec.com/vona2/detail/221000545155/?CategorySpec=00000232425%3A%3Amig00000002020528&list=PageCategory) | 144
106 |  | Square thin nut M4 | TBN-STU-M4 | 9 | 9 | €0.37 | €3.33 | Misumi | 2025-03-26 | 2025-04-22 | https://uk.misumi-ec.com/vona2/detail/221000545155/?CategorySpec=00000232425%3A%3Amig00000002020528&list=PageCategory | 145
107 |  | Slide-in T-slot nut M4 | 6-3-M4 | 2 | 2 | €0.28 | €0.56 | Aluxprofile | 2025-03-26 | 2025-04-03 | https://www.aluxprofile.com/slide-in-t-slot-nut-t-slot-6-m4/a3565?filter=38 | 146
108 |  | Slide-in T-slot nut M5 | 6-3-M5 | 2 | 2 | €0.28 | €0.56 | Aluxprofile | 2025-03-26 | 2025-04-03 | Slide-in T-slot nut, T-slot 6 M5 | Aluxprofile.com (https://www.aluxprofile.com/slide-in-t-slot-nut-t-slot-6-m5/a3566?filter=38) | 147
109 |  | Hammer T-slot nut M5 | 6-1-M5 | 95 | 91 | €0.17 | €16.15 | Aluxprofile | 2025-03-26 | 2025-04-03 | Hammer nut T-slot 6 M5 | Aluxprofile.com (https://www.aluxprofile.com/hammer-nut-t-slot-6-m5/a3536?filter=38) | 148
110 |  | Hammer T-slot nut M4 | 6-1-M4 | 4 | 4 | €0.17 | €0.68 | Aluxprofile | 2025-03-26 | 2025-04-03 | Hammer nut, T-slot 6 M4 | Aluxprofile.com (https://www.aluxprofile.com/hammer-nut-t-slot-6-m4/a3535?filter=38) | 149
111 |  | Hammer T-slot nut M3 | 6-1-M3 | 4 | 4 | €0.17 | €0.68 | Aluxprofile | 2025-03-26 |  | Hammer nut, T-slot 6 M3 | Aluxprofile.com (https://www.aluxprofile.com/hammer-nut-t-slot-6-m3/a3534?filter=38) | 150
112 |  | 20 Hammer T-slot nut M3 | DFC00031 | 1 | 1 | €4.95 | €4.95 | 123-3D |  | 2025-04-22 | https://www.123-3d.nl/123-3D-Glijmoer-M3-t-b-v-aluminium-2020-profiel-20-stuks-123-3D-huismerk-i2059-t14575.html?gad_source=1 | 151
113 |  | Plain washer small M6x0.8mm | WSJS-SUSTBS-M6 | 6 | 6 | €0.13 | €0.78 | Misumi | 2025-03-26 | 2025-04-22 | https://uk.misumi-ec.com/vona2/detail/221000552007/?list=PageCategory | 152
 |  |  |  |  |  |  |  |  |  |  |  | 153
 | subtotal (incl btw) |  |  |  |  |  | €584.81 | €462.00 |  |  |  | 154
 |  |  |  |  |  |  |  |  |  |  |  | 155
 | Total (incl btw) |  |  |  |  |  | €803.71 |  |  |  |  | 156
 | Total (excl btw) |  |  |  |  |  | €634.93 |  |  |  |  | 157

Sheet: Al cut list
Item | Qty | Length
1 | 4 | 575
2 | 4 | 630
3 | 4 | 510
4 | 2 | 530
5 | 2 | 313
6 | 2 | 365
7 | 2 | 501
8 | 2 | 383
 |  | 11044
Name | Value
right_rod | 110
top_rod | 86
bottom_rod | 66
left_rod | 87

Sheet: Wire cut list
Wire Color | Item | Power rating | Voltage Rating | Min Current Rating | exact length (mm) | Number of wires | Safety factor | Cut length | https://www.engineeringtoolbox.com/wire-gauges-d_419.html |  | mm²
Brown | L line | 600 | 220 | 2.7 | 1500 | 1 | 1.5 | 2250 |  |  | 2.5
Blue | N line | 600 | 220 | 2.7 | 800 | 1 | 1.5 | 1200 |  |  | 0.75
Green-yellow | Earth line | 600 | 220 | 2.7 | 800 | 1 | 1.5 | 1200 |  |  | 2.5
Black | PTC voltage in, Motor voltage in, Rest voltage in | 350 | 24 | 14.6 | 200 | 3 | 1.5 | 900 |  |  | 2.5
Red | PTC voltage in, Motor voltage in, Rest voltage in | 350 | 24 | 14.6 | 200 | 3 | 1.5 | 900 |  |  | 2.5
Black | PTC - | 350 | 24 | 14.6 | 350 | 1 | 1.5 | 525 |  |  | 2.5
Red | PTC + | 350 | 24 | 14.6 | 350 | 1 | 1.5 | 525 |  |  | 2.5
black | Fan - | 3 | 24 | 0.1 | 350 | 1 | 1.5 | 525 |  |  | 0.2
red | Fan + | 3 | 24 | 0.1 | 350 | 1 | 1.5 | 525 |  |  | 0.2
blue | Thermistor + | Data | 3 | / | 350 | 1 | 1.5 | 525 |  |  | 0.2
brown | Thermistor - | Data | 3 | / | 350 | 1 | 1.5 | 525 |  |  | 0.2
red | LED + | 8 | 24 | 0.3 | 1720 | 1 | 1.5 | 2580 |  |  | 0.2
black | LED - | 8 | 24 | 0.3 | 1720 | 1 | 1.5 | 2580 |  |  | 0.2
 | Ribbon cable 4x | Data | 3.3/5 | / | 200 | 2 | 1.5 | 600 |  | 1
 | Ribbon cable 5x | Data | 3.3/5 | / | 200 | 1 | 1.5 | 300 |  | 1
Not needed
Stepper motor wires (already 500mm)
Limit switch (already 1m)

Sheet: Cable clips
 |  | 1e maat | 2e maat | 3e maat | 4e maat | 5e maat | 6e maat
Bruin | Live |  | 3
Bruin + geelgroen + blauw | 220V |  |  | 4
Stepper motors |  | 2

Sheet: Soldering list
Nodig van NanoCentre voor solderen van PCB:
Deze lijst
PCB | 1 | 1
Male header pins | Alles | 1
Female header pins | Alles | 1
2 pin male JST connector | 2 | 1
4 pin male JST connector | 4 | 1
5 pin male JST connector | 1 | 1
terminal block | 6 | 1
fuse block | 1 | 1
yellow car fuse | 1 | 1
orange resettable fuse | 1 | 1
n mosfet IRLZ44N | 3 | 1
n mosfet IRLB3034PBF Low RdsOn | 1 | 1
Motor drivers | 2 | 1
Buck converter | 1 | 1
Raspberry Pico | 1 | 1
100nF capacitors | Alles | 1
10kOhm resistors | Alles | 1
Buzzer | 1
heat sink mosfet | 1 | 1
heat sink drivers | 2 | 1
heat sink raspberry | 1 | 1
Main power plug for fuse | 1 | 1
In elektronica labo te zoeken
flyback diodes 1N4007 | 3
4A, 220V glass fuse | 1+
100kOhm resistor 0603 | 1
100Ohm resistor 0603 | 4
Shrink wrap for small wires
Shrink wrap for big wires (connection for PTC heater)
Shrink wrap for LED strip connections
Krimptang lenen?
2 pin female header om te krimpen
Wires

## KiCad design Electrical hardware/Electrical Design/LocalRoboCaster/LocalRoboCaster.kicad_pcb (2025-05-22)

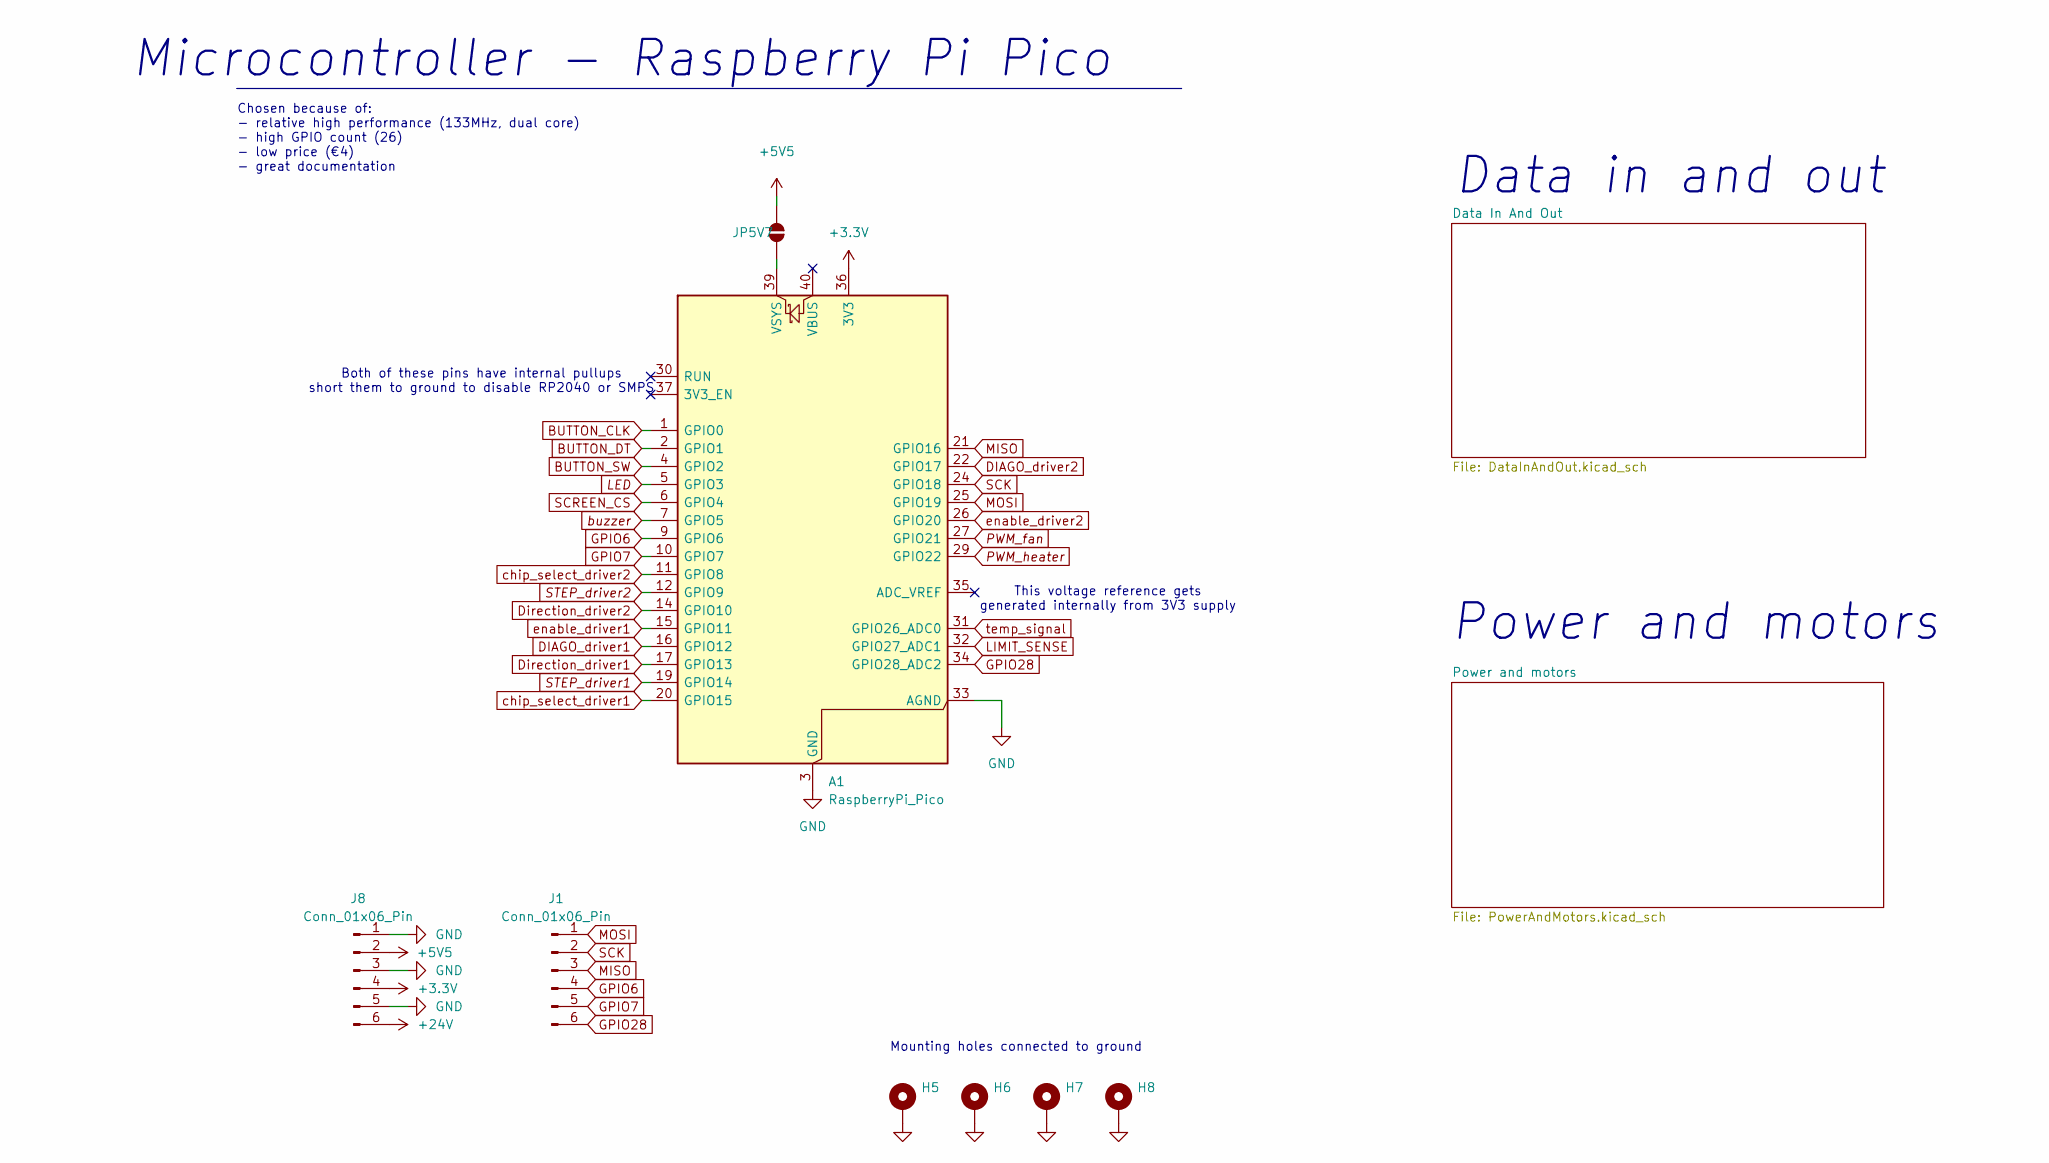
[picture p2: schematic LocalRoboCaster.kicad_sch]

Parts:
A1: RaspberryPi_Pico; Pico
H5, H6, H7, H8: GND; MountingHole_3.2mm_M3_Pad_Via
J1, J8: Conn_01x06_Pin; PinHeader_1x06_P2.54mm_Vertical
JP5V7: SolderJumper_2_Open; SolderJumper-2_P1.3mm_Open_RoundedPad1.0x1.5mm

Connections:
+3.3V: A1.36 (3V3), J8.4; also elsewhere on the board
+5V5: J8.2, JP5V7.2 (B); also elsewhere on the board
+24V: J8.6; also elsewhere on the board
BUTTON_CLK: A1.1 (GPIO0); also elsewhere on the board
BUTTON_DT: A1.2 (GPIO1); also elsewhere on the board
BUTTON_SW: A1.4 (GPIO2); also elsewhere on the board
DIAGO_driver1: A1.16 (GPIO12); also elsewhere on the board
DIAGO_driver2: A1.22 (GPIO17); also elsewhere on the board
Direction_driver1: A1.17 (GPIO13); also elsewhere on the board
Direction_driver2: A1.14 (GPIO10); also elsewhere on the board
GND: A1.3 (GND), A1.8 (GND), A1.13 (GND), A1.18 (GND), A1.23 (GND), A1.28 (GND), A1.33 (AGND), A1.38 (GND), H5.1, H6.1, H7.1, H8.1, J8.1, J8.3, J8.5; also elsewhere on the board
GPIO6: A1.9 (GPIO6), J1.4
GPIO7: A1.10 (GPIO7), J1.5
GPIO28: A1.34 (GPIO28_ADC2), J1.6
LED: A1.5 (GPIO3); also elsewhere on the board
LIMIT_SENSE: A1.32 (GPIO27_ADC1); also elsewhere on the board
MISO: A1.21 (GPIO16), J1.3; also elsewhere on the board
MOSI: A1.25 (GPIO19), J1.1; also elsewhere on the board
unnamed: A1.39 (VSYS), JP5V7.1 (A)
PWM_fan: A1.27 (GPIO21); also elsewhere on the board
PWM_heater: A1.29 (GPIO22); also elsewhere on the board
SCK: A1.24 (GPIO18), J1.2; also elsewhere on the board
SCREEN_CS: A1.6 (GPIO4); also elsewhere on the board
STEP_driver1: A1.19 (GPIO14); also elsewhere on the board
STEP_driver2: A1.12 (GPIO9); also elsewhere on the board
buzzer: A1.7 (GPIO5); also elsewhere on the board
chip_select_driver1: A1.20 (GPIO15); also elsewhere on the board
chip_select_driver2: A1.11 (GPIO8); also elsewhere on the board
enable_driver1: A1.15 (GPIO11); also elsewhere on the board
enable_driver2: A1.26 (GPIO20); also elsewhere on the board
temp_signal: A1.31 (GPIO26_ADC0); also elsewhere on the board

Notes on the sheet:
Microcontroller - Raspberry Pi Pico
Chosen because of: - relative high performance (133MHz, dual core) - high GPIO count (26) - low price (€4) - great documentation
This voltage reference gets generated internally from 3V3 supply
Mounting holes connected to ground
Data in and out
Both of these pins have internal pullups short them to ground to disable RP2040 or SMPS
Power and motors

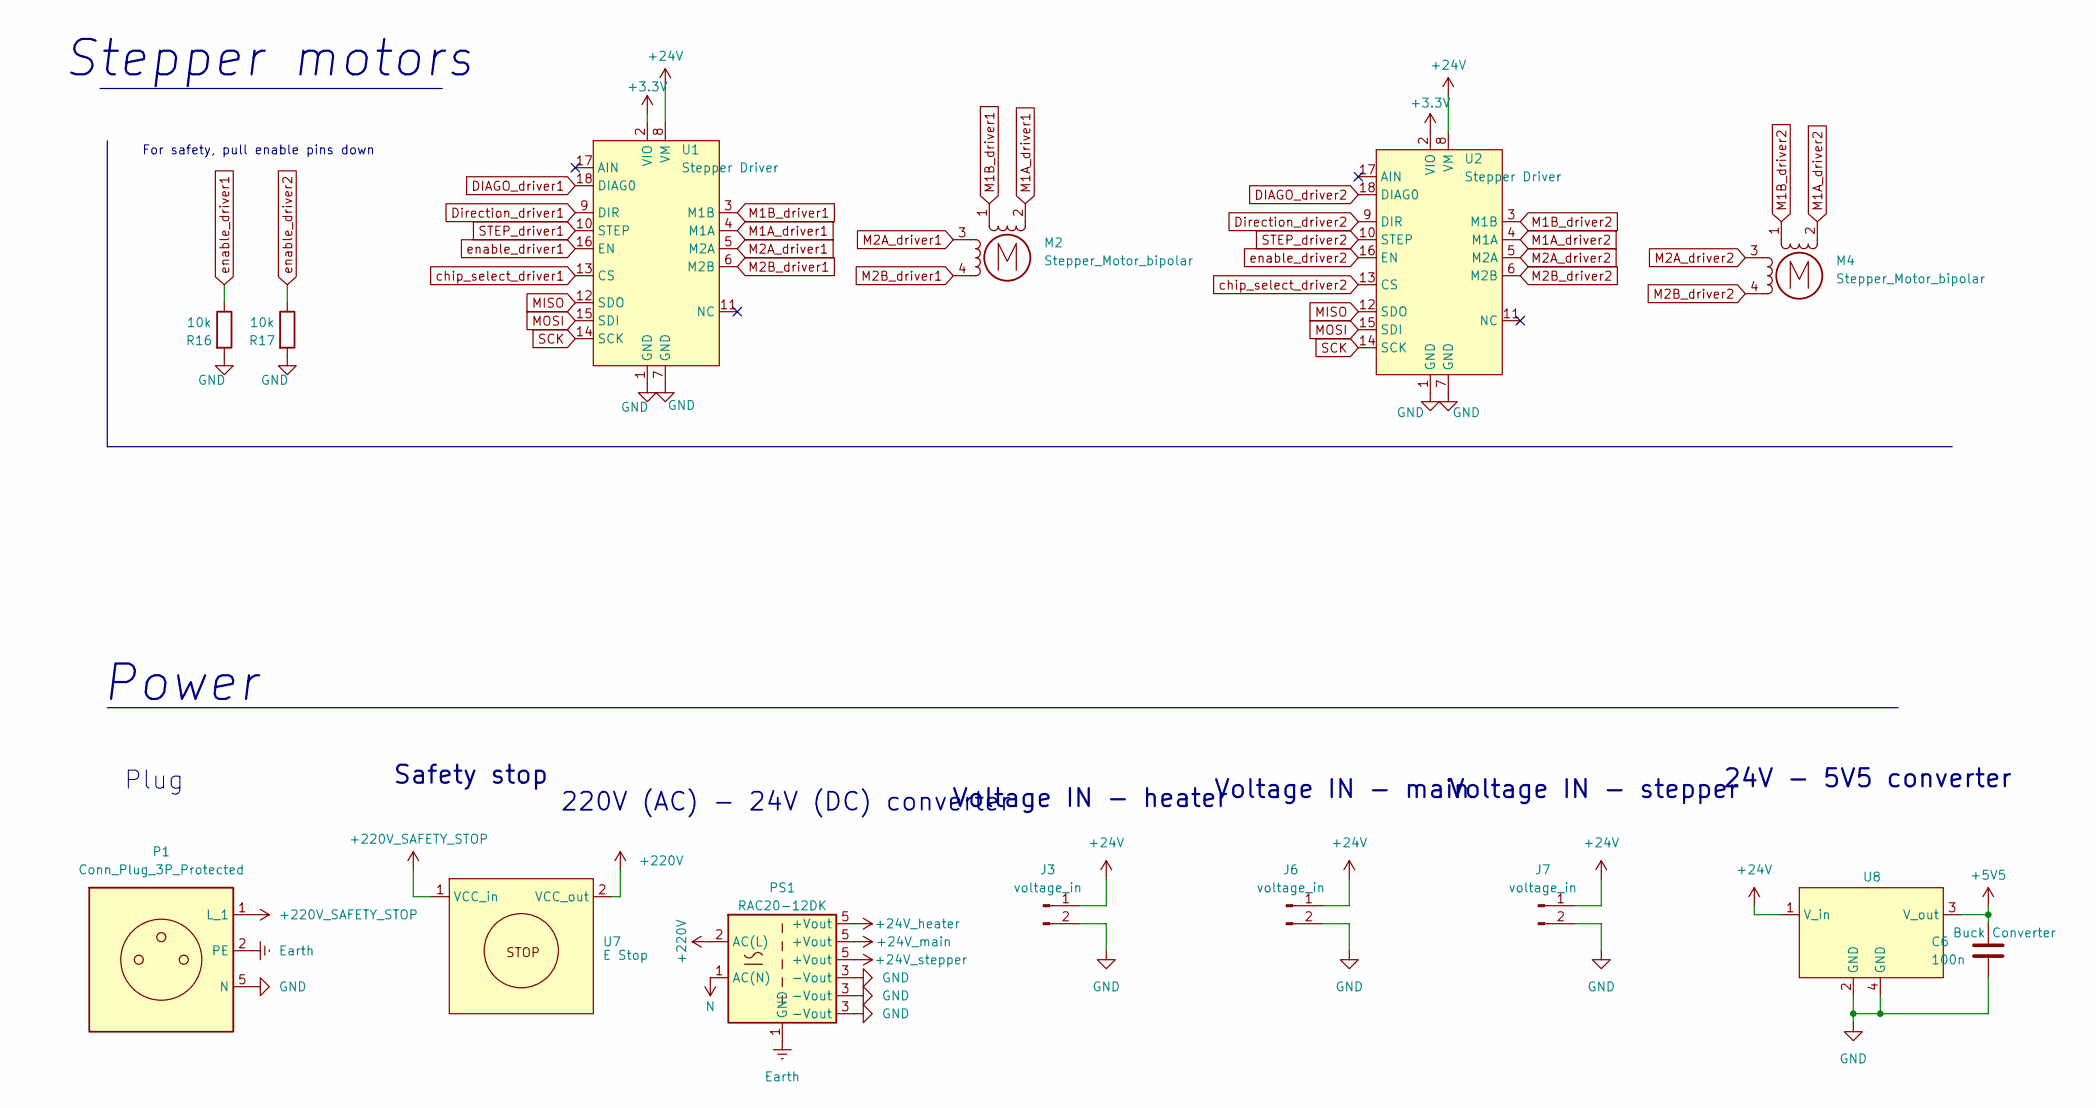
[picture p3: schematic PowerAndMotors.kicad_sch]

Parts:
C6: 100n; C_0603_1608Metric_Pad1.08x0.95mm_HandSolder
J3, J6, J7: voltage_in; TerminalBlock_Phoenix_MKDS-1,5-2-5.08_1x02_P5.08mm_Horizont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
M2, M4: Stepper_Motor_bipolar; JST_XH_B4B-XH-A_1x04_P2.50mm_Vertical
P1: Conn_Plug_3P_Protected
PS1: RAC20-12DK
R16, R17: 10k; R_0603_1608Metric_Pad0.98x0.95mm_HandSolder
U1, U2: Stepper Driver; Pololu_Breakout-16_15.2x20.3mm
U7: E Stop
U8: Buck Converter; LM2596

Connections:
+3.3V: U1.2 (VIO), U2.2 (VIO); also elsewhere on the board
+5V5: C6.1, U8.3 (V_out); also elsewhere on the board
+24V: J3.1, J6.1, J7.1, U1.8 (VM), U2.8 (VM), U8.1 (V_in); also elsewhere on the board
DIAGO_driver1: U1.18 (DIAG0); also elsewhere on the board
DIAGO_driver2: U2.18 (DIAG0); also elsewhere on the board
Direction_driver1: U1.9 (DIR); also elsewhere on the board
Direction_driver2: U2.9 (DIR); also elsewhere on the board
GND: C6.2, J3.2, J6.2, J7.2, P1.5 (N), PS1.3 (-Vout), R16.2, R17.2, U1.1 (GND), U1.7 (GND), U2.1 (GND), U2.7 (GND), U8.2 (GND), U8.4 (GND); also elsewhere on the board
M1A_driver1: M2.2 (-), U1.4 (M1A)
M1A_driver2: M4.2 (-), U2.4 (M1A)
M1B_driver1: M2.1, U1.3 (M1B)
M1B_driver2: M4.1, U2.3 (M1B)
M2A_driver1: M2.3, U1.5 (M2A)
M2A_driver2: M4.3, U2.5 (M2A)
M2B_driver1: M2.4, U1.6 (M2B)
M2B_driver2: M4.4, U2.6 (M2B)
MISO: U1.12 (SDO), U2.12 (SDO); also elsewhere on the board
MOSI: U1.15 (SDI), U2.15 (SDI); also elsewhere on the board
unnamed: P1.1 (L_1), U7.1 (VCC_in)
unnamed: P1.2 (PE), PS1.1 (AC(N))
unnamed: PS1.2 (AC(L)), U7.2 (VCC_out)
SCK: U1.14 (SCK), U2.14 (SCK); also elsewhere on the board
STEP_driver1: U1.10 (STEP); also elsewhere on the board
STEP_driver2: U2.10 (STEP); also elsewhere on the board
chip_select_driver1: U1.13 (CS); also elsewhere on the board
chip_select_driver2: U2.13 (CS); also elsewhere on the board
enable_driver1: R16.1, U1.16 (EN); also elsewhere on the board
enable_driver2: R17.1, U2.16 (EN); also elsewhere on the board

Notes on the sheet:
Plug
Voltage IN - main
Stepper motors
24V - 5V5 converter
Voltage IN - heater
For safety, pull enable pins down
220V (AC) - 24V (DC) converter
Power
Voltage IN - stepper
Safety stop

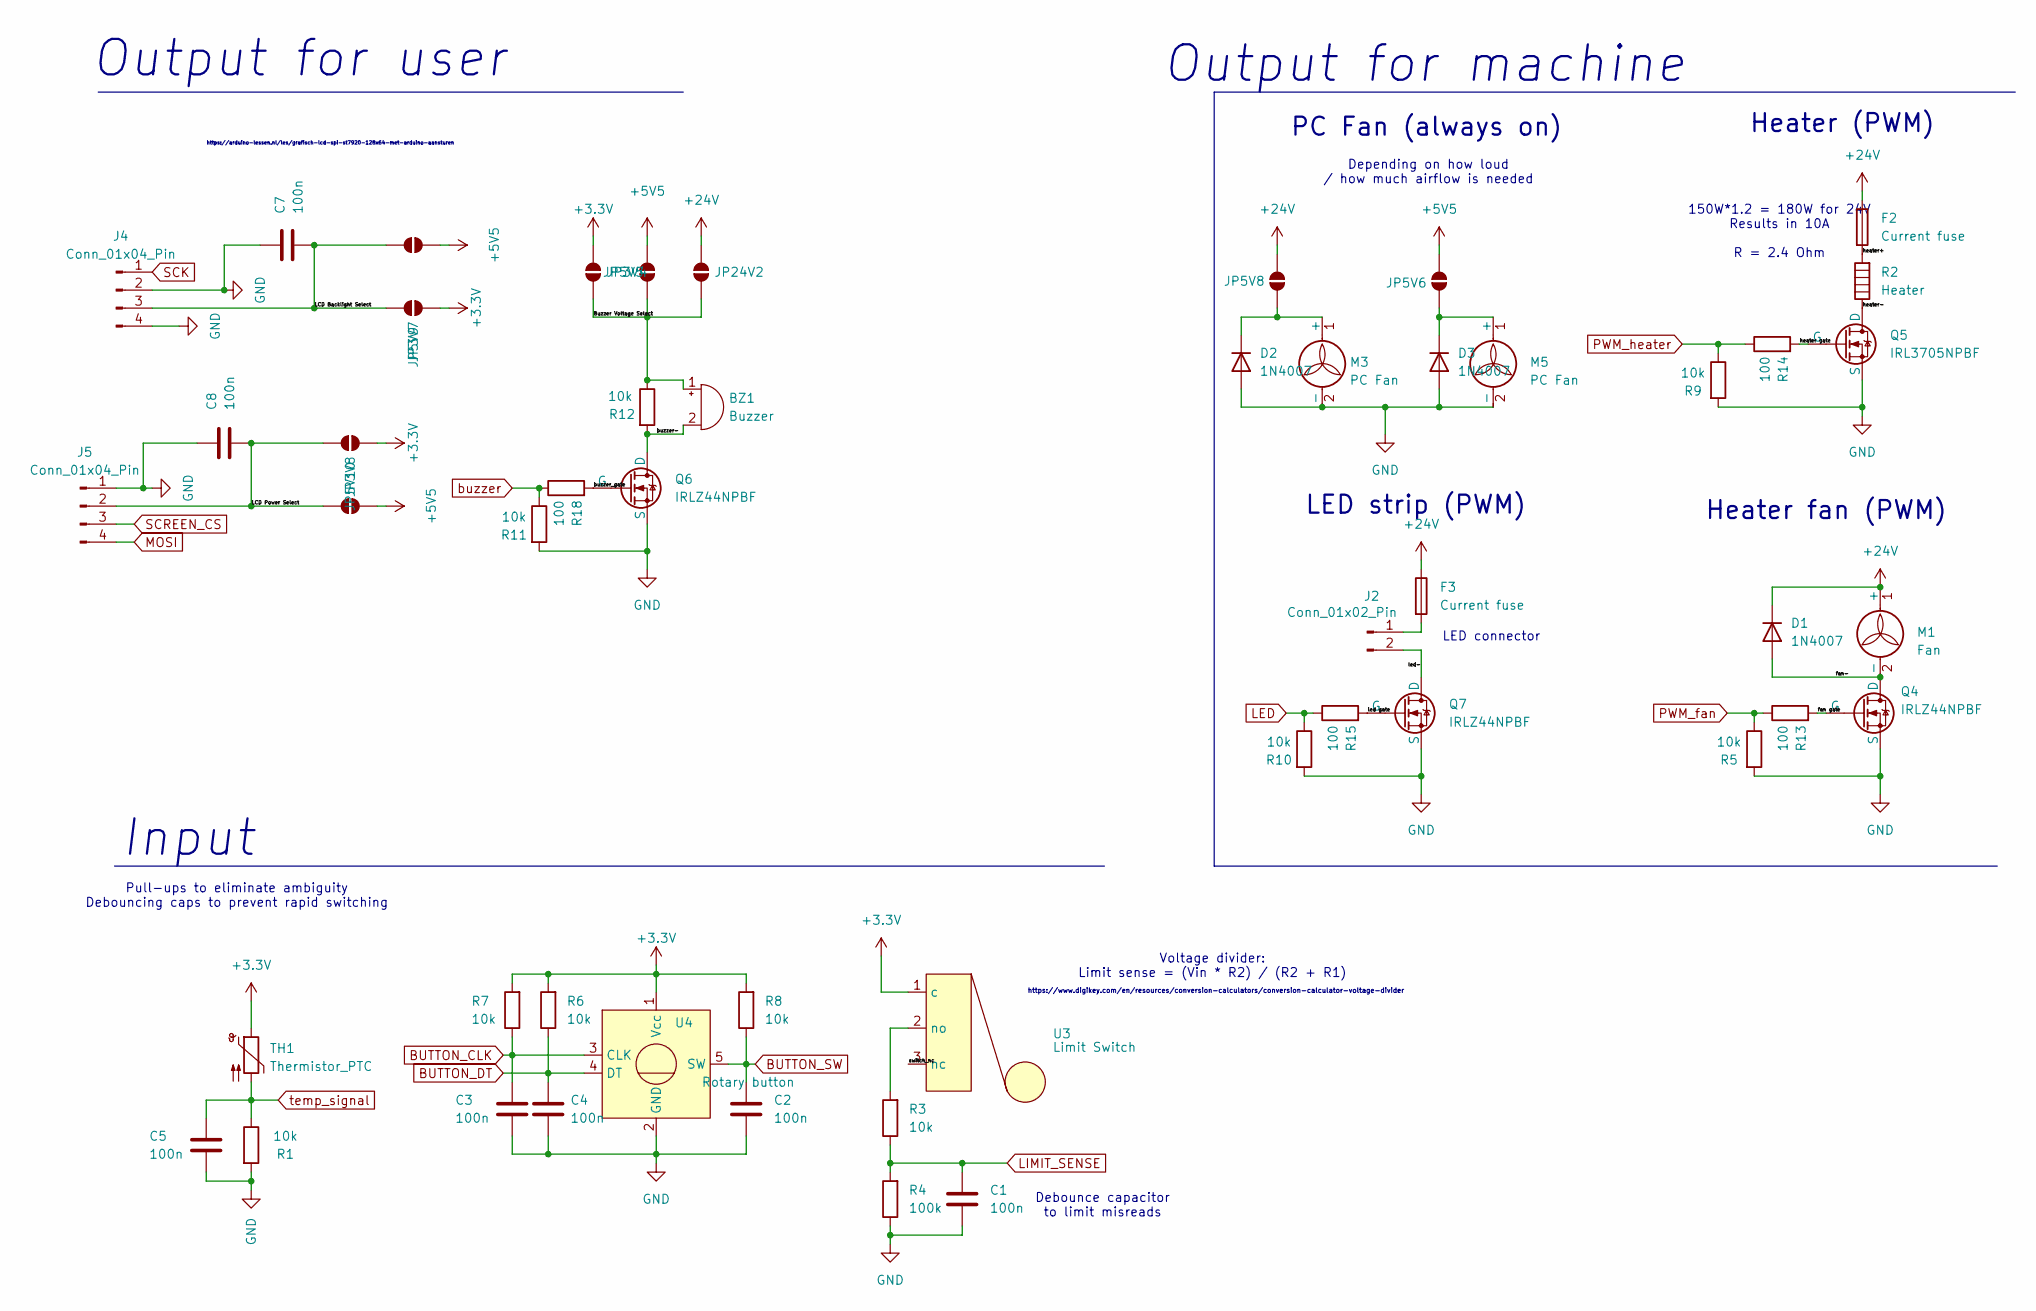
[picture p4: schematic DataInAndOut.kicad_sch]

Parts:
BZ1: Buzzer; Buzzer_12x9.5RM7.6
C1, C2, C3, C4, C5, C7, C8: 100n; C_0603_1608Metric_Pad1.08x0.95mm_HandSolder
D1, D2, D3: 1N4007; D_DO-41_SOD81_P10.16mm_Horizontal
F2: Current fuse; Fuse Holder RS Pro Fuse Blade
F3: Current fuse; Fuse_Bourns_MF-RHT1000
J2: Conn_01x02_Pin; TerminalBlock_Phoenix_MKDS-1,5-2-5.08_1x02_P5.08mm_Horizont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
J4, J5: Conn_01x04_Pin; JST_XH_B4B-XH-A_1x04_P2.50mm_Vertical
JP3V4, JP3V7, JP3V8, JP5V5, JP5V6, JP5V8, JP5V9, JP5V10, JP24V2: SolderJumper_2_Open; SolderJumper-2_P1.3mm_Open_RoundedPad1.0x1.5mm
M1: Fan; TerminalBlock_Phoenix_MKDS-1,5-2-5.08_1x02_P5.08mm_Horizont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
M3, M5: PC Fan; PinHeader_1x02_P2.54mm_Vertical
Q4, Q6, Q7: IRLZ44NPBF; TO-220F-3_Vertical
Q5: IRL3705NPBF; TO-220F-3_Vertical
R1, R3, R5, R6, R7, R8, R9, R10, R11, R12: 10k; R_0603_1608Metric_Pad0.98x0.95mm_HandSolder
R2: Heater; TerminalBlock_Phoenix_MKDS-1,5-2-5.08_1x02_P5.08mm_Horizont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
R4: 100k; R_0603_1608Metric_Pad0.98x0.95mm_HandSolder
R13, R14, R15, R18: 100; R_0603_1608Metric_Pad0.98x0.95mm_HandSolder
TH1: Thermistor_PTC; JST_XH_B2B-XH-A_1x02_P2.50mm_Vertical
U3: Limit Switch; JST_XH_B2B-XH-A_1x02_P2.50mm_Vertical
U4: Rotary button; JST_XH_B5B-XH-A_1x05_P2.50mm_Vertical

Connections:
+3.3V: JP3V4.2 (B), JP3V7.2 (B), JP3V8.2 (B), R6.2, R7.2, R8.2, TH1.1, U3.1 (c), U4.1 (Vcc); also elsewhere on the board
+5V5: JP5V5.2 (B), JP5V6.2 (B), JP5V9.2 (B), JP5V10.2 (B); also elsewhere on the board
+24V: D1.1 (K), F2.1, F3.1, JP5V8.2 (B), JP24V2.2 (B), M1.1 (+); also elsewhere on the board
/Data In And Out/Buzzer Voltage Select: BZ1.1 (+), JP3V4.1 (A), JP5V5.1 (A), JP24V2.1 (A), R12.1
/Data In And Out/LCD Backlight Select: C7.2, J4.3, JP3V7.1 (A), JP5V9.1 (A)
/Data In And Out/LCD Power Select: C8.2, J5.2, JP3V8.1 (A), JP5V10.1 (A)
/Data In And Out/buzzer-: BZ1.2 (-), Q6.1 (D), R12.2
/Data In And Out/buzzer_gate: Q6.2 (G), R18.2
/Data In And Out/fan gate: Q4.2 (G), R13.2
/Data In And Out/fan-: D1.2 (A), M1.2 (-), Q4.1 (D)
/Data In And Out/heater gate: Q5.2 (G), R14.2
/Data In And Out/heater+: F2.2, R2.2
/Data In And Out/heater-: Q5.1 (D), R2.1
/Data In And Out/led gate: Q7.2 (G), R15.2
/Data In And Out/led-: J2.2, Q7.1 (D)
BUTTON_CLK: C3.1, R7.1, U4.3 (CLK); also elsewhere on the board
BUTTON_DT: C4.1, R6.1, U4.4 (DT); also elsewhere on the board
BUTTON_SW: C2.1, R8.1, U4.5 (SW); also elsewhere on the board
GND: C1.2, C2.2, C3.2, C4.2, C5.2, C7.1, C8.1, D2.2 (A), D3.2 (A), J4.2, J4.4, J5.1, M3.2 (-), M5.2 (-), Q4.3 (S), Q5.3 (S), Q6.3 (S), Q7.3 (S), R1.2, R4.1, R5.2, R9.2, R10.2, R11.2, U4.2 (GND); also elsewhere on the board
LED: R10.1, R15.1; also elsewhere on the board
LIMIT_SENSE: C1.1, R3.1, R4.2; also elsewhere on the board
MOSI: J5.4; also elsewhere on the board
unnamed: D2.1 (K), JP5V8.1 (A), M3.1 (+)
unnamed: D3.1 (K), JP5V6.1 (A), M5.1 (+)
unnamed: F3.2, J2.1
unnamed: R3.2, U3.2 (no)
PWM_fan: R5.1, R13.1; also elsewhere on the board
PWM_heater: R9.1, R14.1; also elsewhere on the board
SCK: J4.1; also elsewhere on the board
SCREEN_CS: J5.3; also elsewhere on the board
buzzer: R11.1, R18.1; also elsewhere on the board
temp_signal: C5.1, R1.1, TH1.2; also elsewhere on the board

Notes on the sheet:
PC Fan (always on)
Depending on how loud / how much airflow is needed
Heater (PWM)
https://arduino-lessen.nl/les/grafisch-lcd-spi-st7920-128x64-met-arduino-aansturen
Pull-ups to eliminate ambiguity Debouncing caps to prevent rapid switching
Heater fan (PWM)
LED strip (PWM)
Input
Output for user
150W*1.2 = 180W for 24V Results in 10A R = 2.4 Ohm
Output for machine
LED connector
Debounce capacitor to limit misreads
https://www.digikey.com/en/resources/conversion-calculators/conversion-calculator-voltage-divider
Voltage divider: Limit sense = (Vin * R2) / (R2 + R1)

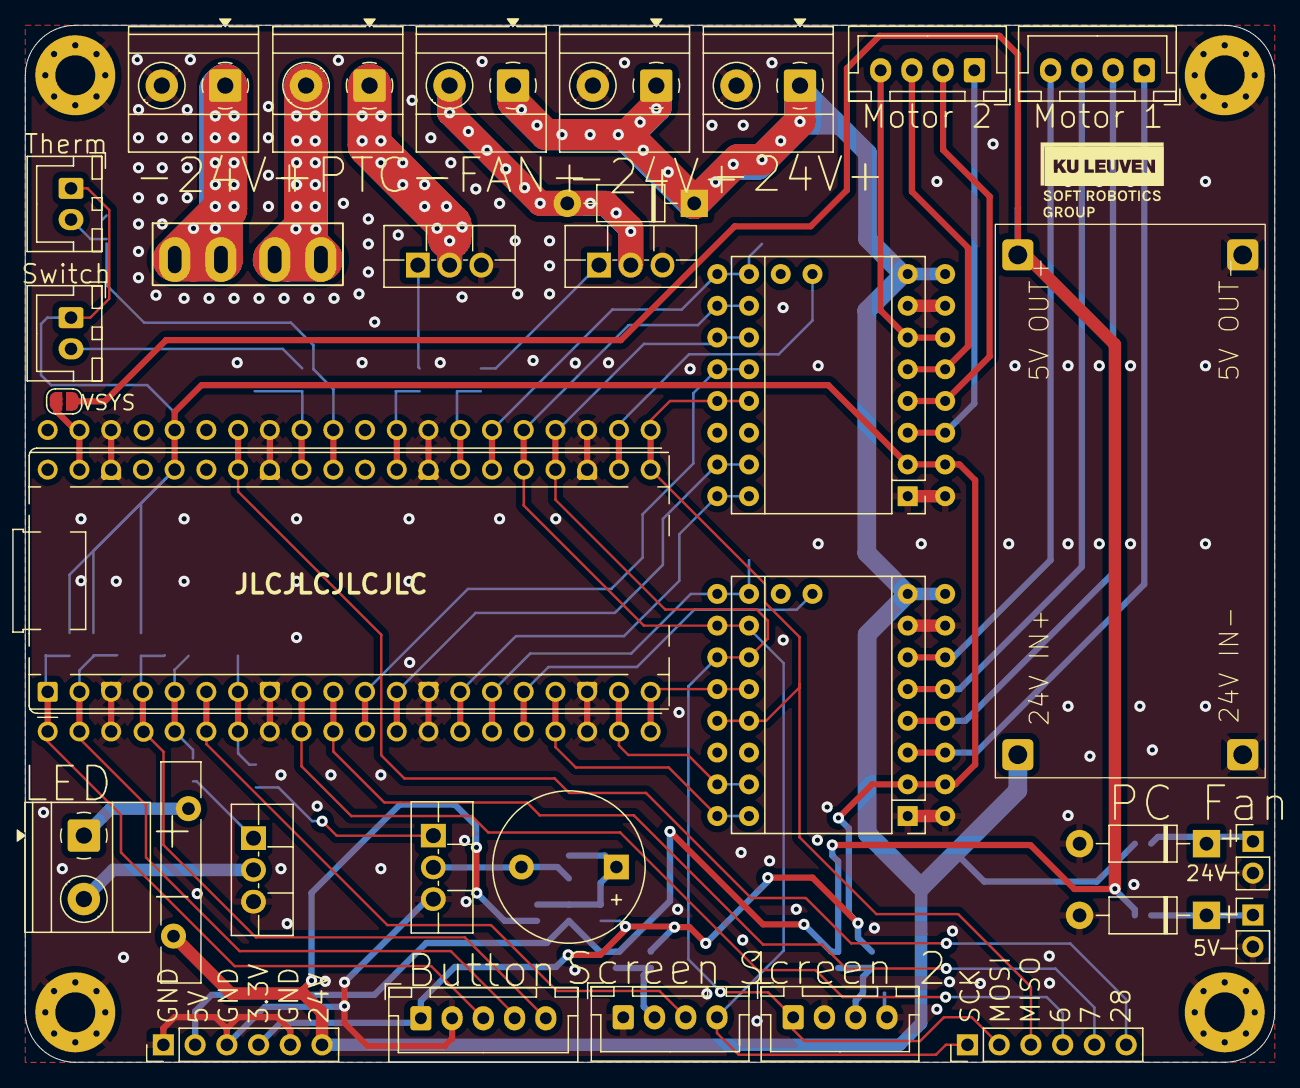
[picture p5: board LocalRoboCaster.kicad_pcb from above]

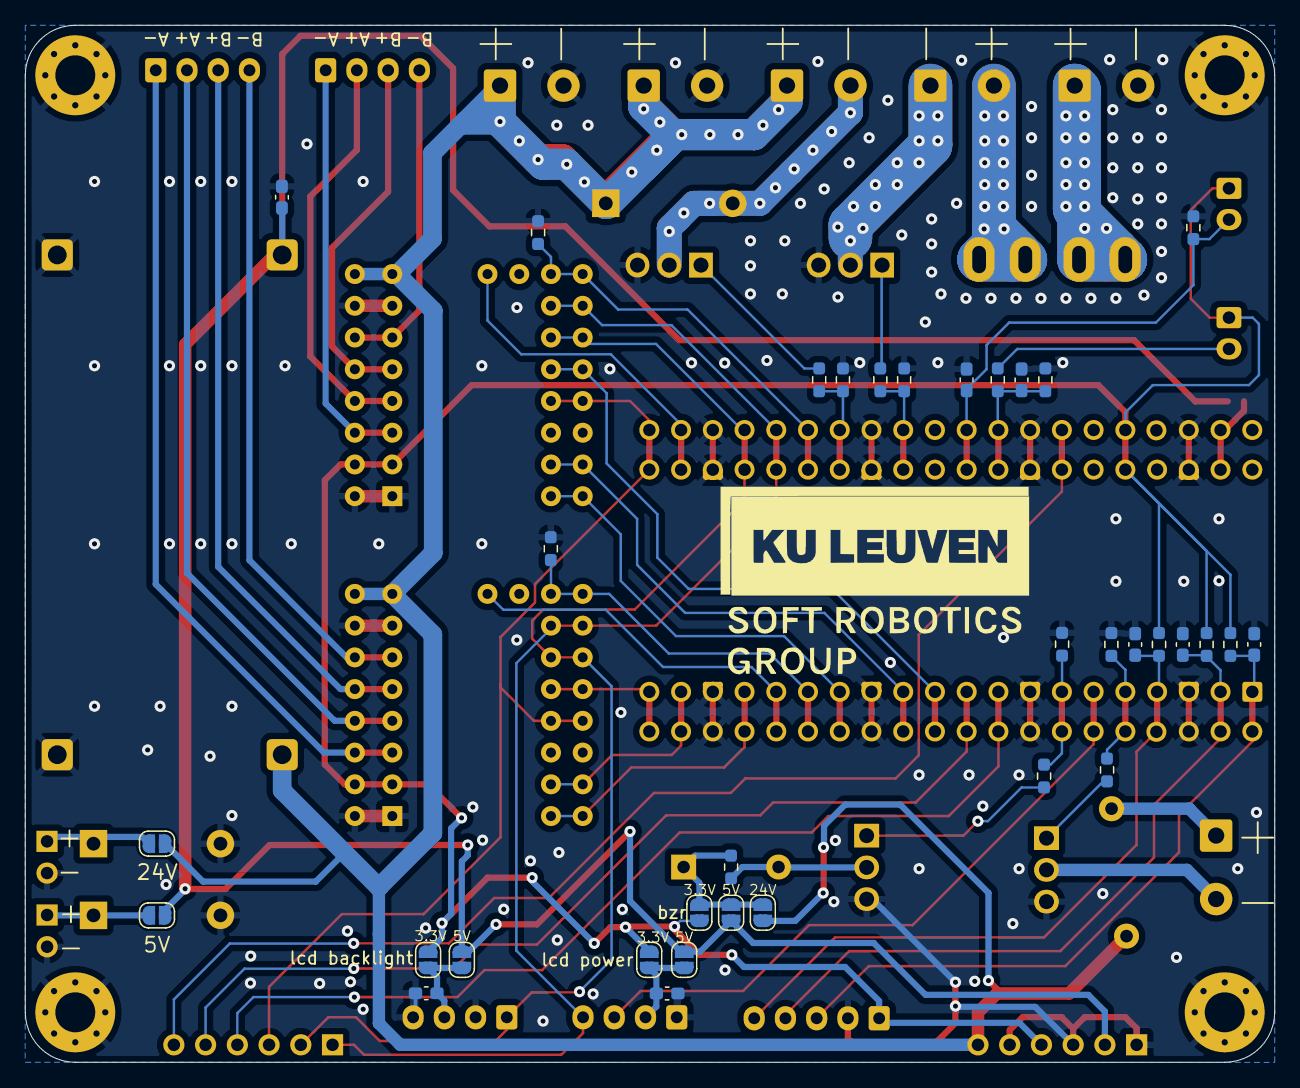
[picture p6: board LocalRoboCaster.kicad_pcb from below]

Board: 2 copper layers, 100.0 x 83.0 mm, 70 parts (34 on the bottom side), 55 nets.

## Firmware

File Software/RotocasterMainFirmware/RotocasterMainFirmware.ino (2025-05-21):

#include <Wire.h>
#include <U8g2lib.h>
#include "bitmaps.h"
#include "hardware/flash.h"
#include "hardware/sync.h"
#include "SmoothLED.h"
#include <ezBuzzer.h> // ezBuzzer library
#include "thermistor.h"
//#include "RP2040_PWM.h"
#include <hardware/irq.h>
#include <hardware/timer.h>




const unsigned int totalHomeOptions = 4;  // Total selectable options (0 = none, 1 = quick start, 2 = preset select)
const unsigned int totalQuickStartOptions = 10;
unsigned int totalPresetSelectOptions = 7;  // cannot be const uint since SD contents is variable
const unsigned int totalPresetAddOptions = 11;
const unsigned int totalPresetInfoOptions = 13;  // Same as presetAdd but needs delete and start operation
const unsigned int totalOperationOptions = 5;
const unsigned int totalWarningOptions = 5;
const unsigned int totalConfirmQuickStartOptions = 2;
const unsigned int totalConfirmPresetOptions = 2;
unsigned int totalPreheatOptions = 3;

int homePointer = 0;        // 0 = none, 1 = Quick Start, 2 = Select Preset
int quickStartPointer = 0;  // 0 = none, 1 = Quick Start, 2 = Select Preset
int presetSelectPointer = 0;
int presetAddPointer = 0;
int presetInfoPointer = 0;
int operationPointer = 0;
int warningPointer = 0;
int confirmQuickStartPointer = 0;
int confirmPresetPointer = 0;
int preheatPointer = 0;
int sensorScreenPointer = 0;

//void drawSensorScreen();

// --------------------------- FLASH ----------------------------------//


#define XIP_BASE 0x10000000
#define FLASH_SECTOR_SIZE 4096
#define FLASH_STORAGE_OFFSET ((1024) * 1024)  // 1.0 MB offset
#define MAX_PRESETS 50                        // Maximum number of presets

const char *adjectives[] = {
  "Squishy", "Flexi", "Soft", "Bendy", "Elastic",
  "Stretch", "Malle", "Comply", "Jelly", "Pliable",
  "Rubbery", "Wobbly", "Cushy", "Yieldy", "Squirmy",
  "Bouncy", "Spongy", "Supple", "Mushy", "Floppy"
};

const char *subjects[] = {
  "Gripper", "Bot", "Hand", "Tendon", "Pad",
  "Arm", "Claw", "Finger", "Limb", "Joint",
  "Digit", "Glove", "Fist", "Wrist", "Elbow",
  "Sensor", "Trigger", "Muscle", "Valve", "Link"
};



struct PresetData {
  char name[16];
  int16_t innerSpeedStart;
  int16_t innerSpeedEnd;
  int16_t outerSpeedStart;
  int16_t outerSpeedEnd;
  int16_t durationHr;
  int16_t durationMin;
  int16_t tempStart;
  int16_t tempEnd;
};

PresetData newPresetAddData;
PresetData lastUsedPresetData;

struct Settings {
  uint8_t version;
  uint8_t brightness;
  uint8_t volume;
};

struct FlashStorage {
  Settings settings;
  uint8_t presetCount;
  PresetData presets[MAX_PRESETS];
};

FlashStorage flashData;

void __not_in_flash_func(writeFlashData)() {
  uint32_t ints = save_and_disable_interrupts();
  flash_range_erase(FLASH_STORAGE_OFFSET, FLASH_SECTOR_SIZE);
  restore_interrupts(ints);

  ints = save_and_disable_interrupts();
  flash_range_program(FLASH_STORAGE_OFFSET, (const uint8_t *)&flashData, sizeof(FlashStorage));
  restore_interrupts(ints);
}

void readFlashData() {
  FlashStorage *dataRead = (FlashStorage *)(XIP_BASE + FLASH_STORAGE_OFFSET);
  if (dataRead->settings.version == 0xFF) {  // Uninitialized flash check
    Serial.println("Flash is empty. Initializing default values.");
    flashData.settings = { 1, 50, 75 };
    flashData.presetCount = 0;
    writeFlashData();
  } else {
    flashData = *dataRead;
  }

  Serial.println("Stored settings:");
  Serial.print("Version: ");
  Serial.println(flashData.settings.version);
  Serial.print("Brightness: ");
  Serial.println(flashData.settings.brightness);
  Serial.print("Volume: ");
  Serial.println(flashData.settings.volume);
  Serial.print("Preset count: ");
  Serial.println(flashData.presetCount);

  for (uint8_t i = 0; i < flashData.presetCount; i++) {
    Serial.print("Preset ");
    Serial.print(i + 1);
    Serial.print(": ");
    Serial.println(flashData.presets[i].name);
  }
}

bool addPreset(PresetData newPreset) {
  if (flashData.presetCount >= MAX_PRESETS) {
    Serial.println("Preset storage full!");
    return false;
  }
  flashData.presets[flashData.presetCount] = newPreset;
  flashData.presetCount++;
  writeFlashData();
  return true;
}


bool updatePreset(PresetData newPreset, uint8_t index) {
  if (index >= flashData.presetCount) {
    Serial.println("Invalid index: no preset exists at that position!");
    return false;
  }

  flashData.presets[index] = newPreset;
  writeFlashData();
  Serial.print("Updated preset at index ");
  Serial.println(index);
  return true;
}


bool saveLastUsedPreset(PresetData newPreset) {
  int8_t lastUsedIndex = -1;

  // Look for a preset containing "LAST USED" in its name
  for (uint8_t i = 0; i < flashData.presetCount; i++) {
    if (strstr(flashData.presets[i].name, "LAST USED") != nullptr) {
      lastUsedIndex = i;
      break;
    }
  }

  // If found, update the preset at that index
  if (lastUsedIndex != -1) {
    flashData.presets[lastUsedIndex] = newPreset;

    // Move it to the front if it's not already there
    if (lastUsedIndex != 0) {
      PresetData temp = flashData.presets[lastUsedIndex];
      // Shift presets from 0 to lastUsedIndex - 1 one step to the right
      for (int i = lastUsedIndex; i > 0; i--) {
        flashData.presets[i] = flashData.presets[i - 1];
      }
      flashData.presets[0] = temp;
    }

    writeFlashData();
    Serial.println("Updated and moved LAST USED preset to front.");
    return true;
  }

  // If not found, check if we can add a new one
  if (flashData.presetCount >= MAX_PRESETS) {
    Serial.println("Preset storage full!");
    return false;
  }

  // Shift all presets to make space at index 0
  for (int i = flashData.presetCount; i > 0; i--) {
    flashData.presets[i] = flashData.presets[i - 1];
  }

  flashData.presets[0] = newPreset;
  flashData.presetCount++;
  totalPresetSelectOptions++;
  writeFlashData();
  Serial.println("Added LAST USED preset at the front.");
  return true;
}


void generateRandomName(char *buffer, size_t length) {
  snprintf(buffer, length, "%s %s", adjectives[random(0, 20)], subjects[random(0, 20)]);
}

// --------------------------- FLASH END ----------------------------------//





// Timer variables
uint32_t lastStateTransitionMillis = 0;
uint32_t lastButtonPressMillis = 0;
uint32_t operationStartMillis = 0;
uint32_t totalOperationMillis = 0;  // Sum of hours and minutes
uint32_t lastRefreshMillis = 0;     // Used for animations on operation screen
uint32_t currentMillis = 0;


// Not using enum because this caused compile errors
#define HOME 0
#define PREHEAT 1
#define PRESET_SELECT 2
#define PRESET_ADD 3
#define PRESET_INFO 4
#define OPERATION 5
#define CONFIRM_QUICK_START 6
#define CONFIRM_PRESET_INFO_START 7
#define CONFIRM_PRESET 8
#define CONFIRM_DELETE 9
#define QUICK_START 10
#define WARNING 11
#define FINISHED_OPERATION 12
#define SENSOR_SCREEN 13


uint8_t CURRENT_SCREEN_STATE = HOME;

enum OperationScreenExtraStates_t {
  OPERATION_NORMAL,
  OPERATION_BACK,
  OPERATION_MOTOR_1,
  OPERATION_MOTOR_2,
  OPERATION_TEMPERATURE,
  OPERATION_INFO,
  OPERATION_TIME
};

OperationScreenExtraStates_t operationScreenExtraState = OPERATION_NORMAL;

// Rotary Encoder Inputs
#define encoderSelectButton 2
#define inputEncoderA 1  // CLK
#define inputEncoderB 0  // DT
#define LED_STRIP_PIN 3
#define SCREEN_CS_PIN 4
#define BUZZER_PIN 5

#define EN_PIN_MOTOR_1 11
#define DIR_PIN_MOTOR_1 13
#define STEP_PIN_MOTOR_1 14
#define CS_PIN_MOTOR_1 15

#define EN_PIN_MOTOR_2 20
#define DIR_PIN_MOTOR_2 10
#define STEP_PIN_MOTOR_2 9
#define CS_PIN_MOTOR_2 8

#define HEATER_PIN 22
#define FAN_PIN 21
#define THERMISTOR_PIN 26

#define LIMIT_SWITCH_PIN 27






int currentStateEncoderA;
int previousStateEncoderA;


bool transitionComplete = false;
bool screenRefreshFlag = true;               // 0 means no refresh is needed, 1 means refresh is needed
volatile bool encoderButtonPressed = false;  // Flag set in ISR
bool preheatEnabledFlag = false;
bool almostExitingOperationFlag = false;
bool finishedOperationFlag = false;
bool editedPresetInfoFlag = false;  // to know wether or not to write to flash when starting operation

bool doorState = false;  // false is closed, true is open
bool heaterFanState = 0;



int preheatTargetTemp = 20;
int tempSelectionValue = 20;
float thermistorTempValue = 21.2;
float averagedThermistorTempValue = thermistorTempValue;
const float thermistorAlpha = 0.1;
uint32_t lastHeaterCalculationMillis = 0xFFFFFFFF;  // start with a giant number, only change it to something reasonable once heater has been turned on

THERMISTOR thermistor(THERMISTOR_PIN,  // Analog pin
                      10000,           // Nominal resistance at 25 ºC
                      3600,            // thermistor's beta coefficient
                      10000);          // Value of the series resistor





// Steppers

void enableSteppers(int, int);
void initializeSteppers(uint8_t, uint8_t);



// RP2040_PWM *PWM1;
// RP2040_PWM *PWM2;


#include <TMC2130Stepper.h>

#define CW 1
#define CCW 0


#define R_SENSE 0.11f  // Match to your driver \
                       // SilentStepStick series use 0.11 \
                       // UltiMachine Einsy and Archim2 boards use 0.2 \
                       // Panucatt BSD2660 uses 0.1 \
                       // Watterott TMC5160 uses 0.075


TMC2130Stepper driver_1 = TMC2130Stepper(EN_PIN_MOTOR_1, DIR_PIN_MOTOR_1, STEP_PIN_MOTOR_1, CS_PIN_MOTOR_1);
TMC2130Stepper driver_2 = TMC2130Stepper(EN_PIN_MOTOR_2, DIR_PIN_MOTOR_2, STEP_PIN_MOTOR_2, CS_PIN_MOTOR_2);



#define MICROSTEP_1 64
#define MICROSTEP_2 64

#define MAX_MILLIAMPS_MOTOR_1 600
#define MAX_MILLIAMPS_MOTOR_2 600

#define maxFrameFreqRPM 30
float stepFrequency1;
float stepFrequency2;

unsigned long microsInterval1;
unsigned long microsInterval2;

volatile bool bitBangStepperActive1;
volatile bool bitBangStepperActive2;





void handleEncoderSelectInterrupt() {
  if (transitionComplete) {       // only after a certain time after the previous interrupt
    encoderButtonPressed = true;  // Set flag when interrupt fires
  }
}




// Scrolling
int startIndex = 0;          // Defines which variable to display first
const int visibleItems = 4;  // Maximum number of visible items on the screen


#define presetNamesLength 16  // 15 alphanumerical, 1 check
const char allowedChars[] = "ABCDEFGHIJKLMNOPQRSTUVWXYZ 0123456789";
const int numAllowedChars = sizeof(allowedChars) - 1;  // subtract the null terminator

// ----- Global Variables ----- //
char stringInput[presetNamesLength] = "NAME           ";  // initial 15-character string (plus '\0')
int currentCharIndex = 0;                                 // Currently selected character position (0 to 9)
bool editingChar = false;                                 // false: moving the cursor; true: editing the character
bool editingName = false;                                 // Needs extra flag because of extra layer of input









#define progressBarTotalLength 124
#define progressBarHeight 2
uint8_t progressBarCurrentPixels = 0;
uint8_t bitmapAnimationCounter = 0;
#define bitmapWidth 19
#define bitmapHeight 19
#define bitmapStartX 1
#define bitmapSpacerX 25
#define bitmapStartY 17

uint32_t remainingHours, remainingMinutes, remainingSeconds;








bool editingValue = false;  // Whether you're editing a value (see quickStart, preheat, ...)
int editingIndex = -1;      // The index of the setting you're currently editing



#define numberOfSettings 8  // Define size at compile time


int16_t quickStartInnerSpeedStart = 1;
int16_t quickStartInnerSpeedEnd = 1;
int16_t quickStartOuterSpeedStart = 4;
int16_t quickStartOuterSpeedEnd = 4;
int16_t quickStartDurationHr = 0;
int16_t quickStartDurationMin = 30;
int16_t quickStartTempStart = 20;
int16_t quickStartTempEnd = 20;
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

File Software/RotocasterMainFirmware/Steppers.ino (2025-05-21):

#define freqThreshold 0

void initializeSteppers(uint8_t microStep1 = 2, uint8_t microStep2 = 2) {
  // Initialize EN and DIR pins.
  pinMode(EN_PIN_MOTOR_1, OUTPUT);
  pinMode(DIR_PIN_MOTOR_1, OUTPUT);
  pinMode(EN_PIN_MOTOR_2, OUTPUT);
  pinMode(DIR_PIN_MOTOR_2, OUTPUT);




  SPI.begin();
  pinMode(MISO, INPUT_PULLUP);

  driver_1.begin();           // Initiate pins and registeries
  driver_1.rms_current(MAX_MILLIAMPS_MOTOR_1);  // Set stepper current to 600mA
  driver_1.stealthChop(1);    // Enable extremely quiet stepping
  driver_1.microsteps(MICROSTEP_1);

  driver_2.begin();           // Initiate pins and registeries
  driver_2.rms_current(MAX_MILLIAMPS_MOTOR_2);  // Set stepper current to 600mA
  driver_2.stealthChop(1);    // Enable extremely quiet stepping
  driver_2.microsteps(MICROSTEP_2);






  // Optionally, initialize them to a known state.
  digitalWrite(EN_PIN_MOTOR_1, HIGH);  // Disabled initially.
  digitalWrite(EN_PIN_MOTOR_2, HIGH);  // Disabled initially.
  setStepperDirections(CW, CW);
}


void setFrequencySteppers(float freq1, float freq2) {
  bool dir1 = CW;
  bool dir2 = CW;
  if (freq1 < 0) {
    dir1 = CCW;
    freq1 = -freq1;
  }
  if (freq2 < 0) {
    dir2 = CCW;
    freq2 = -freq2;
  }
  setStepperDirections(dir1, dir2);
  Serial.print(6000);
  Serial.print("\t");

  Serial.print(freq1);
  Serial.print("\t");
  Serial.println(freq2);
  freq_motor_1 = freq1;
  period_motor_1_us = 1e6 / freq1;
  freq_motor_2 = freq2;
  period_motor_2_us = 1e6 / freq2;
  // PWM1->setPWM(STEP_PIN_MOTOR_1, freq1, 50.0);
  // PWM2->setPWM(STEP_PIN_MOTOR_2, freq2, 50.0);
}

void enableSteppers(int en1 = 1, int en2 = 1) {
  // Zero is on, 1 is off
  digitalWrite(EN_PIN_MOTOR_1, !en1);
  digitalWrite(EN_PIN_MOTOR_2, !en2);
}

void disableSteppers() {
  digitalWrite(EN_PIN_MOTOR_1, HIGH);
  digitalWrite(EN_PIN_MOTOR_2, HIGH);
}

void setStepperDirections(int dir1, int dir2) {
  digitalWrite(DIR_PIN_MOTOR_1, dir1);
  digitalWrite(DIR_PIN_MOTOR_2, dir2);
}


#define MOTOR_STEPS_PER_ROT 180
#define BELT_TRANSMISSION_RATIO 3

// Motor1 maps to inner frame, motor2 maps to outer frame
void calculateStepFrequencies(float &stepFrequency1, float &stepFrequency2, float desiredOuterFrameDPS, float desiredInnerFrameDPS, uint8_t microStep1, uint8_t microStep2) {
  // Conver
  float desiredOuterFrameHz = desiredOuterFrameDPS / 360;
  float desiredInnerFrameHz = desiredInnerFrameDPS / 360;

  // Serial.println(desiredOuterFrameRPM);
  // Serial.println(desiredInnerFrameRPM);
  // Serial.println();

  float desiredOuterMotorShaftHz = desiredOuterFrameHz * BELT_TRANSMISSION_RATIO;
  //float desiredInnerMotorShaftHz = (desiredInnerFrameHz)*BELT_TRANSMISSION_RATIO;

  float desiredInnerMotorShaftHz = (-desiredOuterFrameHz + desiredInnerFrameHz) * BELT_TRANSMISSION_RATIO;


  // stepFrequency1 = constrain(stepFrequency1, 0, 1000);
  // stepFrequency2 = constrain(stepFrequency2, 0, 1000);

  stepFrequency2 = (desiredOuterMotorShaftHz * MOTOR_STEPS_PER_ROT * MICROSTEP_2);
  stepFrequency1 = (desiredInnerMotorShaftHz * MOTOR_STEPS_PER_ROT * MICROSTEP_1);
}
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

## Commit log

2025-05-20 Added Arduino code
2025-05-20 Added 4/5 libraries
    [TMC2130-sample-circuit .fzz, TMC5130_TMC2130_TMC2100_Calculations.xlsx]
2025-05-20 Organized libraries into library folder
    [TMC2130-sample-circuit .fzz, TMC5130_TMC2130_TMC2100_Calculations.xlsx]
2025-05-20 Added hardware documentation
    [DataInAndOut.kicad_sch, LocalRoboCaster-B_Cu.gbr, LocalRoboCaster-B_Mask.gbr, LocalRoboCaster-B_Paste.gbr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]
2025-05-20 Moved Software together in one folder
    [TMC2130-sample-circuit .fzz, TMC5130_TMC2130_TMC2100_Calculations.xlsx]
2025-05-22 Added BOM in mechanical folder
    [BOM.xlsx]
2025-05-22 Added report and improved electrical design files
    [DataInAndOut.kicad_sch, LocalRoboCaster.kicad_pcb]
